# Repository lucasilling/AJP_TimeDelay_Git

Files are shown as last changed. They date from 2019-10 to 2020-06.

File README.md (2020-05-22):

# AJP Time Delay Device Documentation

Supplemental material for article on a programmable electronic delay circuit.

- `assembly-instructions`: A guide to ordering parts and building the device
  yourself.

- `arduino/FIFO_P`: The code uploaded to the Arduino Due.

- `fifo-p3f`: The KiCAD files for the device, as well as a schematic
  PDF and the gerber files that I sent for manufacture.

- `program-rescaling`: The code used to calculate the gain and offset
  resistor values to be optimal, given the constraints of E-series
  values and the overall resistances needed.

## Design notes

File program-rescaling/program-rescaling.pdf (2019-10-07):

# program-rescaling

## August 26, 2019

## 1 Offset and gain calculations for Due DAC to ADC opamps

### 1.1 Voltages that determine required offset and gain

In [1]: V_DL | = 3.3 * 1/6; # V. Due DAC0 minimum voltage
V_DH | = 3.3 * 5/6; # V. Due DAC0 maximum voltage
V_AL | = -2.5; | # V. ADC input minimum voltage
V_AH | = 2.5; | # V. ADC input maximum voltage
offset = ((V_AH + V_AL) - (V_DH + V_DL)) / 2.; # V gain = (V_AH - V_AL) / (V_DH - V_DL); # V/V println("Offset:\t", offset, " V\nGain:\t", gain, " V");
Offset: | -1.65 V
Gain: | 2.2727272727272725 V

### 1.2 Choice of resistor tolerance range (the E-series to use)

In [2]: E3 = [1.0, 2.2, 4.7]; # Very common
E24 = [
| 1.0, 1.1, 1.2, 1.3, 1.5, 1.6, 1.8, 2.0, 2.2, 2.4, 2.7, 3.0, 3.3, 3.6, 3.9, 4.3, 4.7, 5.1, 5.6, 6.2, 6.8, 7.5, 8.2, 9.1

]; # 5% tolerance

In [3]: E_series = E24;

Evaluates f on all possible combinations of resistors in a given E-series.

In [4]: function combinations(E, f)
| span = 1:length(E)
[[f(E[i], E[j]), E[i], E[j]]
| for i in span for j in span] # [[f(x, y), x, y]]
end

Out[4]: combinations (generic function with 1 method)

Finds the nearest E-series value to the value given.

In [5]: function nearest(E, x)
p = floor(log10(x));
y = x / 10^p;
best = first(sort(E, lt = (a, b) -> abs(y - a) < abs(y - b))); best * 10^p;
end

Out[5]: nearest (generic function with 1 method)

### 1.3 Offset component selection calculations

### Improved calculation of the output voltage of the LM4041-ADJ where Vref depends upon VO

(V_Onom here).

In [6]: V_Onom = abs(offset); # V
V_Y = 1.240; # V
∆V_O = V_Onom - V_Y; # V
∆V_ref_∆V_O = -1.55e-3; # V/V. Absolute worst case: -3 mV/V V_ref = V_Y + ∆V_O * ∆V_ref_∆V_O; # V
R2_to_R1 = (V_Onom / V_ref) - 1.; # Ω/Ω

VO(ratio) = V_ref * (ratio + 1.);
println("V_ref = ", V_ref, " V");

V_ref = 1.2393645 V

Selection parameters.

In [7]: ratio_tolerance = 1.; # % RV_off = 1.0e3; # Ω
println("We want a resistor ratio of ", R2_to_R1, " Ω/Ω and ",

ratio_tolerance, "% nominal tolerance.");

We want a resistor ratio of 0.33132746661696366 Ω/Ω and 1.0% nominal tolerance.

Calculate the best resistors to choose to give the best nominal ratio.

In [8]: offset_ratio(x, y, off) = (x + 0.5 * off) / (y + 0.5 * off); # Divide RV_off by 1e3 so that it is at the same scale as the E-series values.
off_ratios | = combinations(E_series,
# [[Ω/Ω, Ω, Ω]]. [[ratio, R2, R1]]

(x, y) -> offset_ratio(x, y, RV_off / 1e3));
off_ratios_tol = filter(x -> ratio_tolerance / 100. > abs(1. - x[1] / R2_to_R1), off_ratios); # [[Ω/Ω, Ω, Ω]]

off_ratios_s = sort(off_ratios_tol, lt = (x, y) -> isless(abs(x[1] - R2_to_R1), abs(y[1] - R2_to_R1))); # [[Ω/Ω, Ω, Ω]]

if (length(off_ratios_s) > 0)
R1 = off_ratios_s[1][3] * 1e3; # Ω
R2 = off_ratios_s[1][2] * 1e3; # Ω

display(off_ratios_s);
println("Best offset resistor values:\n", "R2: ", R2 / 1e3, " kΩ\n",
"R1: ", R1 / 1e3, " kΩ");

else
println("No combinations give a ", ratio_tolerance, "% offset tolerance."); end

3-element Array{Array{Float64,1},1}: [0.333333, 1.1, 4.3]
[0.333333, 2.4, 8.2]
[0.333333, 2.7, 9.1]

Best offset resistor values: R2: 1.1 kΩ
R1: 4.3 kΩ

Calculate the margins of adjustability when a potentiometer is inserted between the two resistors.

In [9]: VO_simple(ratio) = 1.233 * (ratio + 1.);

In [10]: ratio_min = R2 / (R1 + RV_off); ratio_max = (R2 + RV_off) / R1; println("Low:\t", VO(ratio_min), " V"); println("High:\t", VO(ratio_max), " V");
println("S Low:\t", VO_simple(ratio_min), " V");
println("S High:\t", VO_simple(ratio_max), " V");
V_O_low | = VO(ratio_min) - V_Onom; # V. Negative margin away from V_Onom
V_O_high | = VO(ratio_max) - V_Onom; # V. Positive margin away from V_Onom
V_O_total = V_O_high - V_O_low; | # V. Total argin away from V_Onom
println("Offset margins **after amplification** for a ",
RV_off / 1e3, " kΩ potentiometer:\n",
"Low margin:\t", | V_O_low | * 1e3 * gain," mV\t(",
100. * V_O_low | / V_Onom, "%)\n",
"High margin:\t", | V_O_high | * 1e3 * gain, " mV\t(",
100. * V_O_high | / V_Onom, "%)\n",
"Total margin:\t", V_O_total * 1e3 * gain, " mV\t(",
100. * V_O_total / V_Onom, "%)");
Low: | 1.4965910943396226 V
High: | 1.844635534883721 V
S Low: | 1.4889056603773585 V
S High: | 1.8351627906976746 V

Offset margins **after amplification** for a 1.0 kΩ potentiometer:

Low margin: | -348.65660377358483 mV | (-9.297509433962265%)
High margin: | 442.3534883720931 mV | (11.796093023255818%)
Total margin: | 791.010092145678 mV | (21.093602457218083%)

### 1.3.1 LM4041-ADJ resistor selection

In [11]: Vcc_ref = 5.; # V V_R_ref = Vcc_ref - V_Onom; # V R_load = R1 + RV_off + R2; # Ω

I_load = V_Onom / R_load; # A
I_Q = 2.9e-3; # A
I_t = I_Q + I_load;
R_ref = nearest(E_series, V_R_ref / I_t); # Ω

I_ref = V_R_ref / R_ref; # A
println("Best resistor for the LM4041-ADJ (I_load = ", I_load * 1e3, " mA):\n", "R_ref:\t", R_ref / 1e3, " kΩ\n",

"I_ref:\t", I_ref * 1e3, " mA\t(", 100. * (I_ref - I_t) / I_t, "%)\n", "Power:\t", V_R_ref * I_ref * 1e3, " mW");

Best resistor for the LM4041-ADJ (I_load = 0.2578125 mA):
R_ref: | 1.1 kΩ
I_ref: | 3.045454545454546 mA | (-3.558094552651698%)
Power: | 10.202272727272728 mW

### 1.4 Gain component selection calculations

Selection parameters.

In [12]: div_tolerance = 1.; # % RV_gain = 1.0e3 # Ω

#div_nom = 1. / gain;

div_nom = 5.0 / 2.2;
println("We want a resistor divider with a gain of ", div_nom, " V/V and ", div_tolerance, "% nominal tolerance.");

We want a resistor divider with a gain of 2.2727272727272725 V/V and 1.0% nominal tolerance.

Calculate the best resistors to choose to give the best nominal resistor divider.

In [13]: # For noninverting gain configuration
offset_divider(x, y, off) = 1. + (y + 0.5 * off) / (x + 0.5 * off);
# Divide RV_gain by 1e3 so that it is at the same scale as the E-series values. gain_divs = combinations(E_series, # [[Ω/Ω, Ω, Ω]]. [[ratio, Rb, Ra]]

(x, y) -> offset_divider(x, y, RV_gain / 1e3));
gain_divs_tol = filter(x -> div_tolerance / 100. > abs(1. - x[1] / div_nom), gain_divs); # [[Ω/Ω, Ω, Ω]]
gain_divs_s = sort(gain_divs_tol, # [[Ω/Ω, Ω, Ω]]

lt = (x, y) -> isless(abs(x[1] - div_nom), abs(y[1] - div_nom))); if (length(gain_divs_s) > 0)
Ra = gain_divs_s[1][3] * 1e3; # Ω
Rb = gain_divs_s[1][2] * 1e3; # Ω

display(gain_divs_s);
println("Best gain resistor values:\n", "Ra: ", Ra / 1e3, " kΩ\n",
"Rb: ", Rb / 1e3, " kΩ");

else
println("No combinations give a ", div_tolerance, "% gain tolerance."); end

13-element Array{Array{Float64,1},1}: [2.27273, 3.9, 5.1]
[2.27083, 4.3, 5.6]
[2.26829, 3.6, 4.7]
[2.27778, 1.3, 1.8]
[2.28, 2.0, 2.7]
[2.28125, 2.7, 3.6]
[2.26316, 3.3, 4.3]
[2.26087, 1.8, 2.4]
[2.28571, 1.6, 2.2]
[2.25714, 3.0, 3.9]
[2.28846, 4.7, 6.2]
[2.25, 1.1, 1.5]
[2.25, 1.5, 2.0]

Best gain resistor values: Ra: 5.1 kΩ
Rb: 3.9 kΩ

Calculate the margins of adjustability when a potentiometer is inserted between the two resistors.

In [14]: div_min | = Rb / (Ra + Rb + RV_gain);
div_max | = (Rb + RV_gain) / (Ra + Rb + RV_gain);
div_low | = div_min | - div_nom; # V. Negative margin away from V_Onom
div_high | = div_max | - div_nom; # V. Positive margin away from V_Onom
div_total = div_high - div_low; # V. Total margin away from V_Onom println("Gain margins for a ", RV_gain / 1e3, " kΩ potentiometer:\n",
"Low margin:\t", | div_low | * 1e3, " mV\t(",
100. * div_low | / div_nom, "%)\n",
"High margin:\t", | div_high | * 1e3, " mV\t(",
100. * div_high | / div_nom, "%)\n",

"Total margin:\t", div_total * 1e3, " mV\t(",
100. * div_total / div_nom, "%)");

Gain margins for a 1.0 kΩ potentiometer:

Low margin: | -1882.7272727272723 mV | (-82.83999999999999%)
High margin: | -1782.7272727272725 mV | (-78.44%)
Total margin: | 99.99999999999987 mV | (4.399999999999994%)

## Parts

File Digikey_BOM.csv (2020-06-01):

Manufacturer Part Number | Manufacturer | Digi-Key Part Number | Customer Reference | Reference Designator | Packaging | Part Status | Quantity | Unit Price | Extended Price | Quantity Available | Mfg Std Lead Time | Description | RoHS Status | Lead Free Status | REACH Status
LM2940CT-5.0/NOPB | Texas Instruments | LM2940CT-5.0/NOPB-ND |  | U6 | Tube | Active | 1 | 1.53 | $1.53 | 7476 | 6 Weeks | IC REG LINEAR 5V 1A TO220-3 | ROHS3 Compliant | Lead free | REACH Unaffected
LM2776DBVR | Texas Instruments | 296-43957-1-ND |  | U15 | Cut Tape (CT) | Active | 1 | 1.02 | $1.02 | 12481 | 6 Weeks | IC REG CHARGE PUMP INV SOT23 | ROHS3 Compliant | Lead free | REACH Unaffected
AD7840ARSZ | Analog Devices Inc. | AD7840ARSZ-ND |  | U13 | Tube | Active | 1 | 33.39 | $33.39 | 643 | 8 Weeks | IC DAC 14BIT V-OUT 24SSOP | ROHS3 Compliant | Lead free | REACH Unaffected
72V2105L10PFG | Renesas Electronics America Inc. | 800-1511-ND |  | U10 | Tray | Active | 1 | 131.65 | $131.65 | 45 | 13 Weeks | IC FIFO SUPERSYNC 10NS 64-TQFP | ROHS3 Compliant | Lead free | REACH Unaffected
LTC1740CG#PBF | Linear Technology/Analog Devices | LTC1740CG#PBF-ND |  | U5 | Tube | Active | 1 | 41.67 | $41.67 | 53 | 8 Weeks | IC ADC 14BIT PIPELINED 36SSOP | ROHS3 Compliant | Lead free | REACH Unaffected
SN74LVC2G157DCTR | Texas Instruments | 296-13266-1-ND |  | U2 | Cut Tape (CT) | Active | 3 | 0.48 | $1.44 | 3725 | 6 Weeks | IC 2-1LINE DATA SELECT/MUX SM8 | ROHS3 Compliant | Lead free | REACH Unaffected
61C11-01-08-02 | Grayhill Inc. | GH6102-ND |  | SW1 | Bulk | Active | 1 | 25.77 | $25.77 | 559 | 16 Weeks | ROTARY ENCODER OPTICAL 32PPR | RoHS non-compliant | Contains lead | REACH Unaffected
PRPC002SAAN-RC | Sullins Connector Solutions | S1011EC-02-ND | Board to board | U9 | Bag | Active | 2 | 0.08 | $0.16 | 34630 | Not Available | CONN HEADER VERT 2POS 2.54MM | ROHS3 Compliant | Lead free | REACH Unaffected
PJ-002A | CUI Devices | CP-002A-ND |  | J2 | Bag | Active | 1 | 0.6 | $0.60 | 35575 | 11 Weeks | CONN PWR JACK 2X5.5MM SOLDER | RoHS Compliant | Lead free | Not Available
151033RS03000 | Würth Elektronik | 732-5013-ND |  | D1 | Bulk | Active | 1 | 0.17 | $0.17 | 13557 | 14 Weeks | LED RED CLEAR 3MM ROUND T/H | ROHS3 Compliant | Lead free | REACH Unaffected
4440 | Adafruit Industries LLC | 1528-4440-ND | 128x32 OLED | U11 | Bulk | Active | 1 | 12.5 | $12.50 | 1010 | Not Available | I2C OLED DISPLAY STEMMA QWIIC | ROHS3 Compliant | Not Available | Not Available
A000062 | Arduino | 1050-1049-ND |  | U9 | Box | Active | 1 | 37.4 | $37.40 | 653 | Not Available | ARDUINO DUE ATSAM3X8E EVAL BRD | RoHS Compliant | Lead free | Not Available
5-1634503-1 | TE Connectivity AMP Connectors | A97581-ND |  | J1, J4, J5, J7, J8 | Box | Active | 5 | 2.25 | $11.25 | 11968 | Not Available | CONN BNC JACK STR 50 OHM PCB | RoHS Compliant | Lead free | Not Available
TS12A12511DCNR | Texas Instruments | 296-27523-1-ND |  | U1 | Cut Tape (CT) | Active | 1 | 1.45 | $1.45 | 11236 | 6 Weeks | IC SWITCH SGL SPDT ANLG SOT23-8 | ROHS3 Compliant | Lead free | REACH Unaffected
LM4041DYM3-ADJ-TR | Microchip Technology | 576-2573-1-ND |  | U14 | Cut Tape (CT) | Active | 1 | 0.29 | $0.29 | 2170 | 4 Weeks | IC VREF SHUNT 10V 1% SOT23-3 | ROHS3 Compliant | Lead free | REACH Unaffected
TS53YL102MR10 | Vishay Sfernice | TS53YL-1.0KCT-ND |  | RV1, RV3 | Cut Tape (CT) | Active | 2 | 1.87 | $3.74 | 5901 | 17 Weeks | TRIMMER 1K OHM 0.25W GW TOP ADJ | ROHS3 Compliant | Lead free | Not Available
DMP3099L-7 | Diodes Incorporated | DMP3099L-7DICT-ND |  | Q1 | Cut Tape (CT) | Active | 1 | 0.33 | $0.33 | 183767 | 23 Weeks | MOSFET P-CH 30V SOT23 | ROHS3 Compliant | Lead free | REACH Unaffected
SN74LVC1G04DBVR | Texas Instruments | 296-11599-1-ND |  | U7 | Cut Tape (CT) | Active | 1 | 0.32 | $0.32 | 85313 | 6 Weeks | IC INVERTER 1CH 1-INP SOT23-5 | ROHS3 Compliant | Lead free | REACH Unaffected
SN74LVC1G08DBVR | Texas Instruments | 296-11601-1-ND |  | U12 | Cut Tape (CT) | Active | 1 | 0.26 | $0.26 | 97419 | 6 Weeks | IC GATE AND 1CH 2-INP SOT23-5 | ROHS3 Compliant | Lead free | REACH Unaffected
08055C104KAT2A | AVX Corporation | 478-1395-1-ND | 0u1 | C8, C9, C10, C15, C16, C22, C46,C23, C28, C30, C32, C37, C38 | Cut Tape (CT) | Active | 20 | 0.083 | $1.66 | 36630219 | 12 Weeks | CAP CER 0.1UF 50V X7R 0805 | ROHS3 Compliant | Lead free | REACH Unaffected
08053C105KAT2A | AVX Corporation | 478-5030-1-ND | 1u | C1, C3, C4, C6, C19, C20, C40, C41,C11, C12, C13, C14, C21, C25, C35, C39 | Cut Tape (CT) | Active | 20 | 0.176 | $3.52 | 559518 | 16 Weeks | CAP CER 1UF 25V X7R 0805 | ROHS3 Compliant | Lead free | REACH Unaffected
CL21A106KAYNNNE | Samsung Electro-Mechanics | 1276-2891-1-ND | 10u | C5, C7, C17, C18, C26, C27, C42, C43, C44, C45,C24, C29, C31, C33 | Cut Tape (CT) | Active | 20 | 0.19 | $3.80 | 2116302 | 22 Weeks | CAP CER 10UF 25V X5R 0805 | ROHS3 Compliant | Lead free | REACH Unaffected
08055A102JAT2A | AVX Corporation | 478-1328-1-ND | 1n | C2,C34, C47 | Cut Tape (CT) | Active | 10 | 0.126 | $1.26 | 303649 | 12 Weeks | CAP CER 1000PF 50V C0G/NP0 0805 | ROHS3 Compliant | Lead free | REACH Unaffected
RC0805FR-0749R9L | Yageo | 311-49.9CRCT-ND |  | R1, R3, R4, R19 | Cut Tape (CT) | Active | 4 | 0.1 | $0.40 | 1707550 | 33 Weeks | RES SMD 49.9 OHM 1% 1/8W 0805 | ROHS3 Compliant | Lead free | REACH Unaffected
RC0805FR-0722RL | Yageo | 311-22.0CRCT-ND |  | R2, R6, R20 | Cut Tape (CT) | Active | 3 | 0.1 | $0.30 | 235480 | 33 Weeks | RES SMD 22 OHM 1% 1/8W 0805 | ROHS3 Compliant | Lead free | REACH Unaffected
RC0805FR-07220RL | Yageo | 311-220CRCT-ND |  | R5 | Cut Tape (CT) | Active | 1 | 0.1 | $0.10 | 1267440 | 33 Weeks | RES SMD 220 OHM 1% 1/8W 0805 | ROHS3 Compliant | Lead free | REACH Unaffected
RC0805FR-075K1L | Yageo | 311-5.10KCRCT-ND |  | R7, R9, R10, R11, R13, R16, R17, R18 | Cut Tape (CT) | Active | 10 | 0.04 | $0.40 | 2672 | 33 Weeks | RES SMD 5.1K OHM 1% 1/8W 0805 | ROHS3 Compliant | Lead free | REACH Unaffected
RC0805FR-071K1L | Yageo | 311-1.10KCRCT-ND |  | R8, R14 | Cut Tape (CT) | Active | 2 | 0.1 | $0.20 | 745483 | 33 Weeks | RES SMD 1.1K OHM 1% 1/8W 0805 | ROHS3 Compliant | Lead free | REACH Unaffected
RC0805FR-073K9L | Yageo | 311-3.90KCRCT-ND |  | R15 | Cut Tape (CT) | Active | 1 | 0.1 | $0.10 | 643670 | 33 Weeks | RES SMD 3.9K OHM 1% 1/8W 0805 | ROHS3 Compliant | Lead free | REACH Unaffected
RC0805FR-074K3L | Yageo | 311-4.30KCRCT-ND |  | R12 | Cut Tape (CT) | Active | 1 | 0.1 | $0.10 | 238177 | 33 Weeks | RES SMD 4.3K OHM 1% 1/8W 0805 | ROHS3 Compliant | Lead free | REACH Unaffected
LM1117IDTX-3.3/NOPB | Texas Instruments | LM1117IDTX-3.3/NOPBCT-ND |  | U8 | Cut Tape (CT) | Active | 1 | 1.44 | $1.44 | 21823 | 6 Weeks | IC REG LINEAR 3.3V 800MA TO252-3 | ROHS3 Compliant | Lead free | REACH Unaffected
TL082CDR | Texas Instruments | 296-1284-1-ND |  | U16 | Cut Tape (CT) | Active | 1 | 0.41 | $0.41 | 12716 | 6 Weeks | IC OPAMP JFET 2 CIRCUIT 8SOIC | ROHS3 Compliant | Lead free | REACH Unaffected
OSTTC082162 | On Shore Technology Inc. | ED2615-ND |  | J3 | Bulk | Active | 1 | 1.72 | $1.72 | 1723 | 8 Weeks | TERM BLK 8P SIDE ENT 5.08MM PCB | ROHS3 Compliant | Lead free | REACH Unaffected
54102-S08-18 | Amphenol ICC (FCI) | 609-5600-ND | Board to board | U9 | Bulk | Active | 1 | 1.45 | $1.45 | 197 | 9 Weeks | CONN HEADER VERT 36POS 2.54MM | RoHS non-compliant | Contains lead | Not Available
PRPC003SAAN-RC | Sullins Connector Solutions | S1011EC-03-ND | Board to board | U9 | Bag | Active | 1 | 0.12 | $0.12 | 11543 | Not Available | CONN HEADER VERT 3POS 2.54MM | ROHS3 Compliant | Lead free | REACH Unaffected
PRPC006SAAN-RC | Sullins Connector Solutions | S1011EC-06-ND | Board to board | U9 | Bag | Active | 1 | 0.19 | $0.19 | 2550 | Not Available | CONN HEADER VERT 6POS 2.54MM | ROHS3 Compliant | Lead free | REACH Unaffected
LPPB042CFFN-RC | Sullins Connector Solutions | S9009E-04-ND | Board to board | U9 | Tube | Active | 1 | 1.05 | $1.05 | 2828 | 5 Weeks | CONN HDR 8POS 0.05 GOLD PCB | ROHS3 Compliant | Lead free | REACH Unaffected
RC0805JR-070RL | Yageo | 311-0.0ARCT-ND | Jumpers |  | Cut Tape (CT) | Active | 10 | 0.035 | $0.35 | 11238049 | 24 Weeks | RES SMD 0 OHM JUMPER 1/8W 0805 | ROHS3 Compliant | Lead free | REACH Unaffected
3296W-1-103LF | Bourns Inc. | 3296W-103LF-ND |  | RV2 | Tube | Active | 1 | 2.41 | $2.41 | 4469 | 6 Weeks | TRIMMER 10K OHM 0.5W PC PIN TOP | ROHS3 Compliant | Lead free | REACH Unaffected

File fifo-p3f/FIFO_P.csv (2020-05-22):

Source: | /home/jfjhh/Documents/AJP_TimeDelay_Git/fifo-p3f/FIFO_P.sch
Date: | Thu 21 May 2020 10:44:45 PM EDT
Tool: | Eeschema 5.1.6
Generator: | /usr/share/kicad/plugins/bom_csv_grouped_by_value.py
Component Count: | 96
Individual Components:
Item | Qty | Reference(s) | Value | LibPart | Footprint | Datasheet
 |  | C1 | 1u | Device:C_Small | Capacitor_SMD:C_0805_2012Metric_Pad1.15x1.40mm_HandSolder
 |  | C2 | 1n | Device:C_Small | Capacitor_SMD:C_0805_2012Metric_Pad1.15x1.40mm_HandSolder
 |  | C3 | 1u | Device:C_Small | Capacitor_SMD:C_0805_2012Metric_Pad1.15x1.40mm_HandSolder
 |  | C4 | 1u | Device:C_Small | Capacitor_SMD:C_0805_2012Metric_Pad1.15x1.40mm_HandSolder
 |  | C5 | 10u | Device:C | Capacitor_SMD:C_0805_2012Metric_Pad1.15x1.40mm_HandSolder
 |  | C6 | 1u | Device:C_Small | Capacitor_SMD:C_0805_2012Metric_Pad1.15x1.40mm_HandSolder
 |  | C7 | 10u | Device:C | Capacitor_SMD:C_0805_2012Metric_Pad1.15x1.40mm_HandSolder
 |  | C8 | 0u1 | Device:C | Capacitor_SMD:C_0805_2012Metric_Pad1.15x1.40mm_HandSolder
 |  | C9 | 0u1 | Device:C | Capacitor_SMD:C_0805_2012Metric_Pad1.15x1.40mm_HandSolder
 |  | C10 | 0u1 | Device:C | Capacitor_SMD:C_0805_2012Metric_Pad1.15x1.40mm_HandSolder
 |  | C11 | 1u | Device:C | Capacitor_SMD:C_0805_2012Metric_Pad1.15x1.40mm_HandSolder
 |  | C12 | 1u | Device:C | Capacitor_SMD:C_0805_2012Metric_Pad1.15x1.40mm_HandSolder
 |  | C13 | 1u | Device:C | Capacitor_SMD:C_0805_2012Metric_Pad1.15x1.40mm_HandSolder
 |  | C14 | 1u | Device:C | Capacitor_SMD:C_0805_2012Metric_Pad1.15x1.40mm_HandSolder
 |  | C15 | 0u1 | Device:C | Capacitor_SMD:C_0805_2012Metric_Pad1.15x1.40mm_HandSolder | ~
 |  | C16 | 0u1 | Device:C | Capacitor_SMD:C_0805_2012Metric_Pad1.15x1.40mm_HandSolder | ~
 |  | C17 | 10u | Device:C | Capacitor_SMD:C_0805_2012Metric_Pad1.15x1.40mm_HandSolder
 |  | C18 | 10u | Device:C | Capacitor_SMD:C_0805_2012Metric_Pad1.15x1.40mm_HandSolder
 |  | C19 | 1u | Device:C_Small | Capacitor_SMD:C_0805_2012Metric_Pad1.15x1.40mm_HandSolder
 |  | C20 | 1u | Device:C_Small | Capacitor_SMD:C_0805_2012Metric_Pad1.15x1.40mm_HandSolder
 |  | C21 | 1u | Device:C | Capacitor_SMD:C_0805_2012Metric_Pad1.15x1.40mm_HandSolder
 |  | C22 | 0u1 | Device:C | Capacitor_SMD:C_0805_2012Metric_Pad1.15x1.40mm_HandSolder | ~
 |  | C23 | 0u1 | Device:C_Small | Capacitor_SMD:C_0805_2012Metric_Pad1.15x1.40mm_HandSolder
 |  | C24 | 10u | Device:C_Small | Capacitor_SMD:C_0805_2012Metric_Pad1.15x1.40mm_HandSolder
 |  | C25 | 1u | Device:C | Capacitor_SMD:C_0805_2012Metric_Pad1.15x1.40mm_HandSolder
 |  | C26 | 10u | Device:C | Capacitor_SMD:C_0805_2012Metric_Pad1.15x1.40mm_HandSolder
 |  | C27 | 10u | Device:C | Capacitor_SMD:C_0805_2012Metric_Pad1.15x1.40mm_HandSolder
 |  | C28 | 0u1 | Device:C_Small | Capacitor_SMD:C_0805_2012Metric_Pad1.15x1.40mm_HandSolder
 |  | C29 | 10u | Device:C_Small | Capacitor_SMD:C_0805_2012Metric_Pad1.15x1.40mm_HandSolder
 |  | C30 | 0u1 | Device:C_Small | Capacitor_SMD:C_0805_2012Metric_Pad1.15x1.40mm_HandSolder
 |  | C31 | 10u | Device:C_Small | Capacitor_SMD:C_0805_2012Metric_Pad1.15x1.40mm_HandSolder
 |  | C32 | 0u1 | Device:C_Small | Capacitor_SMD:C_0805_2012Metric_Pad1.15x1.40mm_HandSolder
 |  | C33 | 10u | Device:C_Small | Capacitor_SMD:C_0805_2012Metric_Pad1.15x1.40mm_HandSolder
 |  | C34 | 1n | Device:C | Capacitor_SMD:C_0805_2012Metric_Pad1.15x1.40mm_HandSolder | ~
 |  | C35 | 1u | Device:C | Capacitor_SMD:C_0805_2012Metric_Pad1.15x1.40mm_HandSolder | ~
 |  | C37 | 0u1 | Device:C_Small | Capacitor_SMD:C_0805_2012Metric_Pad1.15x1.40mm_HandSolder | ~
 |  | C38 | 0u1 | Device:C_Small | Capacitor_SMD:C_0805_2012Metric_Pad1.15x1.40mm_HandSolder | ~
 |  | C39 | 1u | Device:C | Capacitor_SMD:C_0805_2012Metric_Pad1.15x1.40mm_HandSolder | ~
 |  | C40 | 1u | Device:C_Small | Capacitor_SMD:C_0805_2012Metric_Pad1.15x1.40mm_HandSolder | ~
 |  | C41 | 1u | Device:C_Small | Capacitor_SMD:C_0805_2012Metric_Pad1.15x1.40mm_HandSolder | ~
 |  | C42 | 10u | Device:C | Capacitor_SMD:C_0805_2012Metric_Pad1.15x1.40mm_HandSolder | ~
 |  | C43 | 10u | Device:C | Capacitor_SMD:C_0805_2012Metric_Pad1.15x1.40mm_HandSolder | ~
 |  | C44 | 10u | Device:C | Capacitor_SMD:C_0805_2012Metric_Pad1.15x1.40mm_HandSolder | ~
 |  | C45 | 10u | Device:C | Capacitor_SMD:C_0805_2012Metric_Pad1.15x1.40mm_HandSolder | ~
 |  | C46 | 0u1 | Device:C | Capacitor_SMD:C_0805_2012Metric_Pad1.15x1.40mm_HandSolder | ~
 |  | C47 | 1n | Device:C | Capacitor_SMD:C_0805_2012Metric_Pad1.15x1.40mm_HandSolder | ~
 |  | D1 | LED_RED | Device:LED | LED_THT:LED_D3.0mm
 |  | J1 | Vin | Connector:Conn_Coaxial | Connector_Coaxial:BNC_TEConnectivity_1478204_Vertical | ~
 |  | J2 | Jack-DC | Connector:Jack-DC | Connector_BarrelJack:BarrelJack_Horizontal | ~
 |  | J3 | Screw_Terminal_01x08 | Connector:Screw_Terminal_01x08 | TerminalBlock_Phoenix:TerminalBlock_Phoenix_MKDS-3-8-5.08_1x08_P5.08mm_Horizontal | ~
 |  | J4 | XWCLK | Connector:Conn_Coaxial | Connector_Coaxial:BNC_TEConnectivity_1478204_Vertical | ~
 |  | J5 | XRCLK | Connector:Conn_Coaxial | Connector_Coaxial:BNC_TEConnectivity_1478204_Vertical | ~
 |  | J6 | Conn_02x04_Odd_Even | Connector_Generic:Conn_02x04_Odd_Even | Connector_PinSocket_1.27mm:PinSocket_2x04_P1.27mm_Vertical | ~
 |  | J7 | Start Trigger | Connector:Conn_Coaxial | Connector_Coaxial:BNC_TEConnectivity_1478204_Vertical | ~
 |  | J8 | Vout | Connector:Conn_Coaxial | Connector_Coaxial:BNC_TEConnectivity_1478204_Vertical | ~
 |  | Q1 | DMP3099L | FIFO_P:DMP3099L | Package_TO_SOT_SMD:SOT-23 | https://www.diodes.com/assets/Datasheets/DMP3013SFV.pdf
 |  | R1 | 49R9 | Device:R | Resistor_SMD:R_0805_2012Metric_Pad1.15x1.40mm_HandSolder
 |  | R2 | 22R | Device:R | Resistor_SMD:R_0805_2012Metric_Pad1.15x1.40mm_HandSolder | ~
 |  | R3 | 49R9 | Device:R | Resistor_SMD:R_0805_2012Metric_Pad1.15x1.40mm_HandSolder
 |  | R4 | 49R9 | Device:R | Resistor_SMD:R_0805_2012Metric_Pad1.15x1.40mm_HandSolder
 |  | R5 | 220R | Device:R | Resistor_SMD:R_0805_2012Metric_Pad1.15x1.40mm_HandSolder
 |  | R6 | 22R | Device:R | Resistor_SMD:R_0805_2012Metric_Pad1.15x1.40mm_HandSolder | ~
 |  | R7 | 5k1 | Device:R | Resistor_SMD:R_0805_2012Metric_Pad1.15x1.40mm_HandSolder
 |  | R8 | 1k1 | Device:R | Resistor_SMD:R_0805_2012Metric_Pad1.15x1.40mm_HandSolder | ~
 |  | R9 | 5k1 | Device:R | Resistor_SMD:R_0805_2012Metric_Pad1.15x1.40mm_HandSolder
 |  | R10 | 5k1 | Device:R | Resistor_SMD:R_0805_2012Metric_Pad1.15x1.40mm_HandSolder
 |  | R11 | 5k1 | Device:R | Resistor_SMD:R_0805_2012Metric_Pad1.15x1.40mm_HandSolder | ~
 |  | R12 | 4k3 | Device:R | Resistor_SMD:R_0805_2012Metric_Pad1.15x1.40mm_HandSolder | ~
 |  | R13 | 5k1 | Device:R | Resistor_SMD:R_0805_2012Metric_Pad1.15x1.40mm_HandSolder | ~
 |  | R14 | 1k1 | Device:R | Resistor_SMD:R_0805_2012Metric_Pad1.15x1.40mm_HandSolder | ~
 |  | R15 | 3k9 | Device:R | Resistor_SMD:R_0805_2012Metric_Pad1.15x1.40mm_HandSolder | ~
 |  | R16 | 5k1 | Device:R | Resistor_SMD:R_0805_2012Metric_Pad1.15x1.40mm_HandSolder | ~
 |  | R17 | 5k1 | Device:R | Resistor_SMD:R_0805_2012Metric_Pad1.15x1.40mm_HandSolder | ~
 |  | R18 | 5k1 | Device:R | Resistor_SMD:R_0805_2012Metric_Pad1.15x1.40mm_HandSolder | ~
 |  | R19 | 49R9 | Device:R | Resistor_SMD:R_0805_2012Metric_Pad1.15x1.40mm_HandSolder | ~
 |  | R20 | 22R | Device:R | Resistor_SMD:R_0805_2012Metric_Pad1.15x1.40mm_HandSolder | ~
 |  | RV1 | 1k | Device:R_POT | Potentiometer_SMD:Potentiometer_Vishay_TS53YL_Vertical | ~
 |  | RV2 | 10k | Device:R_POT | Potentiometer_THT:Potentiometer_Bourns_3296W_Vertical | ~
 |  | RV3 | 1k | Device:R_POT | Potentiometer_SMD:Potentiometer_Vishay_TS53YL_Vertical | ~
 |  | SW1 | Rotary_Encoder_61C | FIFO_P:Rotary_Encoder_61C | FIFO_P:Rotary_Encoder_61C
 |  | U1 | TS12A12511 | FIFO_P:TS12A12511 | Package_TO_SOT_SMD:SOT-23-8_Handsoldering
 |  | U2 | SN74LVC2G157_MUX_TI | FIFO_P:SN74LVC2G157_MUX_TI | Package_SO:SSOP-8_2.95x2.8mm_P0.65mm
 |  | U3 | SN74LVC2G157_MUX_TI | FIFO_P:SN74LVC2G157_MUX_TI | Package_SO:SSOP-8_2.95x2.8mm_P0.65mm
 |  | U4 | SN74LVC2G157_MUX_TI | FIFO_P:SN74LVC2G157_MUX_TI | Package_SO:SSOP-8_2.95x2.8mm_P0.65mm
 |  | U5 | LTC1740 | FIFO_P:LTC1740 | FIFO_P:SSOP-36_5.3mm_Pitch0.65mm
 |  | U6 | LM2940CT-5.0 | FIFO_P:LM2940CT-5.0 | Package_TO_SOT_THT:TO-220-3_Horizontal_TabDown
 |  | U7 | 74LVC1G04 | 74xGxx:74LVC1G04 | Package_TO_SOT_SMD:SOT-23-5_HandSoldering | http://www.ti.com/lit/sg/scyt129e/scyt129e.pdf
 |  | U8 | LM1117-3.3 | Regulator_Linear:LM1117-3.3 | Package_TO_SOT_SMD:TO-252-3_TabPin2 | http://www.ti.com/lit/ds/symlink/lm1117.pdf
 |  | U9 | ARDUINO_DUE_FIFO_P_COMMANDS | FIFO_P:ARDUINO_DUE_FIFO_P_COMMANDS | FIFO_P:Arduino_Due_Selected_Pins
 |  | U10 | IDT_72V2105 | FIFO_P:IDT_72V2105 | FIFO_P:LQFP-64_14x14mm_P0.8mm_HandSolder
 |  | U11 | Adafruit_128x32_OLED_I2C_1306 | FIFO_P:Adafruit_128x32_OLED_I2C_1306 | FIFO_P:Adafruit_128x32_OLED_I2C_1306
 |  | U12 | 74LVC1G08 | 74xGxx:74LVC1G08 | Package_TO_SOT_SMD:SOT-23-5_HandSoldering | http://www.ti.com/lit/sg/scyt129e/scyt129e.pdf
 |  | U13 | AD7840 | FIFO_P:AD7840 | Package_SO:SSOP-24_5.3x8.2mm_P0.65mm
 |  | U14 | LM4041LP-ADJ | Reference_Voltage:LM4041LP-ADJ | Package_TO_SOT_SMD:SOT-23_Handsoldering | http://www.ti.com/lit/ds/symlink/lm4041-n.pdf
 |  | U15 | LM2776 | Regulator_SwitchedCapacitor:LM2776 | Package_TO_SOT_SMD:SOT-23-6 | http://www.ti.com/lit/ds/symlink/lm2776.pdf
 |  | U16 | TL082 | Amplifier_Operational:TL082 | Package_SO:SOIC-8_3.9x4.9mm_P1.27mm | http://www.ti.com/lit/ds/symlink/tl081.pdf
Collated Components:
Item | Qty | Reference(s) | Value | LibPart | Footprint | Datasheet
1 | 8 | C1, C3, C4, C6, C19, C20, C40, C41 | 1u | Device:C_Small | Capacitor_SMD:C_0805_2012Metric_Pad1.15x1.40mm_HandSolder | ~
2 | 1 | C2 | 1n | Device:C_Small | Capacitor_SMD:C_0805_2012Metric_Pad1.15x1.40mm_HandSolder
3 | 10 | C5, C7, C17, C18, C26, C27, C42, C43, C44, C45 | 10u | Device:C | Capacitor_SMD:C_0805_2012Metric_Pad1.15x1.40mm_HandSolder | ~
4 | 7 | C8, C9, C10, C15, C16, C22, C46 | 0u1 | Device:C | Capacitor_SMD:C_0805_2012Metric_Pad1.15x1.40mm_HandSolder | ~
5 | 8 | C11, C12, C13, C14, C21, C25, C35, C39 | 1u | Device:C | Capacitor_SMD:C_0805_2012Metric_Pad1.15x1.40mm_HandSolder | ~
6 | 6 | C23, C28, C30, C32, C37, C38 | 0u1 | Device:C_Small | Capacitor_SMD:C_0805_2012Metric_Pad1.15x1.40mm_HandSolder | ~
7 | 4 | C24, C29, C31, C33 | 10u | Device:C_Small | Capacitor_SMD:C_0805_2012Metric_Pad1.15x1.40mm_HandSolder
8 | 2 | C34, C47 | 1n | Device:C | Capacitor_SMD:C_0805_2012Metric_Pad1.15x1.40mm_HandSolder | ~
9 | 1 | D1 | LED_RED | Device:LED | LED_THT:LED_D3.0mm
10 | 1 | J1 | Vin | Connector:Conn_Coaxial | Connector_Coaxial:BNC_TEConnectivity_1478204_Vertical | ~
11 | 1 | J2 | Jack-DC | Connector:Jack-DC | Connector_BarrelJack:BarrelJack_Horizontal | ~
12 | 1 | J3 | Screw_Terminal_01x08 | Connector:Screw_Terminal_01x08 | TerminalBlock_Phoenix:TerminalBlock_Phoenix_MKDS-3-8-5.08_1x08_P5.08mm_Horizontal | ~
13 | 1 | J4 | XWCLK | Connector:Conn_Coaxial | Connector_Coaxial:BNC_TEConnectivity_1478204_Vertical | ~
14 | 1 | J5 | XRCLK | Connector:Conn_Coaxial | Connector_Coaxial:BNC_TEConnectivity_1478204_Vertical | ~
15 | 1 | J6 | Conn_02x04_Odd_Even | Connector_Generic:Conn_02x04_Odd_Even | Connector_PinSocket_1.27mm:PinSocket_2x04_P1.27mm_Vertical | ~
16 | 1 | J7 | Start Trigger | Connector:Conn_Coaxial | Connector_Coaxial:BNC_TEConnectivity_1478204_Vertical | ~
17 | 1 | J8 | Vout | Connector:Conn_Coaxial | Connector_Coaxial:BNC_TEConnectivity_1478204_Vertical | ~
18 | 1 | Q1 | DMP3099L | FIFO_P:DMP3099L | Package_TO_SOT_SMD:SOT-23 | https://www.diodes.com/assets/Datasheets/DMP3013SFV.pdf
19 | 4 | R1, R3, R4, R19 | 49R9 | Device:R | Resistor_SMD:R_0805_2012Metric_Pad1.15x1.40mm_HandSolder | ~
20 | 3 | R2, R6, R20 | 22R | Device:R | Resistor_SMD:R_0805_2012Metric_Pad1.15x1.40mm_HandSolder | ~
21 | 1 | R5 | 220R | Device:R | Resistor_SMD:R_0805_2012Metric_Pad1.15x1.40mm_HandSolder
22 | 8 | R7, R9, R10, R11, R13, R16, R17, R18 | 5k1 | Device:R | Resistor_SMD:R_0805_2012Metric_Pad1.15x1.40mm_HandSolder | ~
23 | 2 | R8, R14 | 1k1 | Device:R | Resistor_SMD:R_0805_2012Metric_Pad1.15x1.40mm_HandSolder | ~
24 | 1 | R12 | 4k3 | Device:R | Resistor_SMD:R_0805_2012Metric_Pad1.15x1.40mm_HandSolder | ~
25 | 1 | R15 | 3k9 | Device:R | Resistor_SMD:R_0805_2012Metric_Pad1.15x1.40mm_HandSolder | ~
26 | 2 | RV1, RV3 | 1k | Device:R_POT | Potentiometer_SMD:Potentiometer_Vishay_TS53YL_Vertical | ~
27 | 1 | RV2 | 10k | Device:R_POT | Potentiometer_THT:Potentiometer_Bourns_3296W_Vertical | ~
28 | 1 | SW1 | Rotary_Encoder_61C | FIFO_P:Rotary_Encoder_61C | FIFO_P:Rotary_Encoder_61C
29 | 1 | U1 | TS12A12511 | FIFO_P:TS12A12511 | Package_TO_SOT_SMD:SOT-23-8_Handsoldering
30 | 3 | U2, U3, U4 | SN74LVC2G157_MUX_TI | FIFO_P:SN74LVC2G157_MUX_TI | Package_SO:SSOP-8_2.95x2.8mm_P0.65mm
31 | 1 | U5 | LTC1740 | FIFO_P:LTC1740 | FIFO_P:SSOP-36_5.3mm_Pitch0.65mm
32 | 1 | U6 | LM2940CT-5.0 | FIFO_P:LM2940CT-5.0 | Package_TO_SOT_THT:TO-220-3_Horizontal_TabDown
33 | 1 | U7 | 74LVC1G04 | 74xGxx:74LVC1G04 | Package_TO_SOT_SMD:SOT-23-5_HandSoldering | http://www.ti.com/lit/sg/scyt129e/scyt129e.pdf
34 | 1 | U8 | LM1117-3.3 | Regulator_Linear:LM1117-3.3 | Package_TO_SOT_SMD:TO-252-3_TabPin2 | http://www.ti.com/lit/ds/symlink/lm1117.pdf
35 | 1 | U9 | ARDUINO_DUE_FIFO_P_COMMANDS | FIFO_P:ARDUINO_DUE_FIFO_P_COMMANDS | FIFO_P:Arduino_Due_Selected_Pins
36 | 1 | U10 | IDT_72V2105 | FIFO_P:IDT_72V2105 | FIFO_P:LQFP-64_14x14mm_P0.8mm_HandSolder
37 | 1 | U11 | Adafruit_128x32_OLED_I2C_1306 | FIFO_P:Adafruit_128x32_OLED_I2C_1306 | FIFO_P:Adafruit_128x32_OLED_I2C_1306
38 | 1 | U12 | 74LVC1G08 | 74xGxx:74LVC1G08 | Package_TO_SOT_SMD:SOT-23-5_HandSoldering | http://www.ti.com/lit/sg/scyt129e/scyt129e.pdf
39 | 1 | U13 | AD7840 | FIFO_P:AD7840 | Package_SO:SSOP-24_5.3x8.2mm_P0.65mm
40 | 1 | U14 | LM4041LP-ADJ | Reference_Voltage:LM4041LP-ADJ | Package_TO_SOT_SMD:SOT-23_Handsoldering | http://www.ti.com/lit/ds/symlink/lm4041-n.pdf
41 | 1 | U15 | LM2776 | Regulator_SwitchedCapacitor:LM2776 | Package_TO_SOT_SMD:SOT-23-6 | http://www.ti.com/lit/ds/symlink/lm2776.pdf
42 | 1 | U16 | TL082 | Amplifier_Operational:TL082 | Package_SO:SOIC-8_3.9x4.9mm_P1.27mm | http://www.ti.com/lit/ds/symlink/tl081.pdf

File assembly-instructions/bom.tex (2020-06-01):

\begin{tabular}{llllll}
\toprule
Manufacturer Part Number & Digi-Key Part Number& Customer Reference & Reference Designator                                                  & Quantity & Extended Price \\
\midrule
LM2940CT-5.0/NOPB   & LM2940CT-5.0/NOPB-ND     &                & U6                                                                        & 1    & 1.53   \\
LM2776DBVR          & 296-43957-1-ND           &                & U15                                                                       & 1    & 1.02   \\
AD7840ARSZ          & AD7840ARSZ-ND            &                & U13                                                                       & 1    & 33.39  \\
72V2105L10PFG       & 800-1511-ND              &                & U10                                                                       & 1    & 131.65 \\
LTC1740CG\#PBF      & LTC1740CG\#PBF-ND        &                & U5                                                                        & 1    & 41.67  \\
SN74LVC2G157DCTR    & 296-13266-1-ND           &                & U2                                                                        & 3    & 1.44   \\
4440                & 1528-4440-ND             & 128x32 OLED    & U11                                                                       & 1    & 12.50  \\
TS12A12511DCNR      & 296-27523-1-ND           &                & U1                                                                        & 1    & 1.45   \\
LM4041DYM3-ADJ-TR   & 576-2573-1-ND            &                & U14                                                                       & 1    & 0.29   \\
SN74LVC1G04DBVR     & 296-11599-1-ND           &                & U7                                                                        & 1    & 0.32   \\
SN74LVC1G08DBVR     & 296-11601-1-ND           &                & U12                                                                       & 1    & 0.26   \\
LM1117IDTX-3.3/NOPB & LM1117IDTX-3.3/NOPBCT-ND &                & U8                                                                        & 1    & 1.44   \\
TL082CDR            & 296-1284-1-ND            &                & U16                                                                       & 1    & 0.41   \\
A000062             & 1050-1049-ND             &                & U9                                                                        & 1    & 37.40  \\
PRPC002SAAN-RC      & S1011EC-02-ND            & Board to board & U9                                                                        & 2    & 0.16   \\
54102-S08-18        & 609-5600-ND              & Board to board & U9                                                                        & 1    & 1.45   \\
PRPC003SAAN-RC      & S1011EC-03-ND            & Board to board & U9                                                                        & 1    & 0.12   \\
PRPC006SAAN-RC      & S1011EC-06-ND            & Board to board & U9                                                                        & 1    & 0.19   \\
LPPB042CFFN-RC      & S9009E-04-ND             & Board to board & U9                                                                        & 1    & 1.05   \\
DMP3099L-7          & DMP3099L-7DICT-ND        &                & Q1                                                                        & 1    & 0.33   \\
151033RS03000       & 732-5013-ND              &                & D1                                                                        & 1    & 0.17   \\
61C11-01-08-02      & GH6102-ND                &                & SW1                                                                       & 1    & 25.77  \\
5-1634503-1         & A97581-ND                &                & J1, J4, J5, J7, J8                                                        & 5    & 11.25  \\
PJ-002A             & CP-002A-ND               &                & J2                                                                        & 1    & 0.60   \\
OSTTC082162         & ED2615-ND                &                & J3                                                                        & 1    & 1.72   \\
TS53YL102MR10       & TS53YL-1.0KCT-ND         &                & RV1, RV3                                                                  & 2    & 3.74   \\
3296W-1-103LF       & 3296W-103LF-ND           &                & RV2                                                                       & 1    & 2.41   \\
RC0805FR-0749R9L    & 311-49.9CRCT-ND          &                & R1, R3, R4, R19                                                           & 4    & 0.40   \\
RC0805FR-0722RL     & 311-22.0CRCT-ND          &                & R2, R6, R20                                                               & 3    & 0.30   \\
RC0805FR-07220RL    & 311-220CRCT-ND           &                & R5                                                                        & 1    & 0.10   \\
RC0805FR-075K1L     & 311-5.10KCRCT-ND         &                & R7, R9, R10, R11, R13, R16, R17, R18                                      & 10   & 0.40   \\
RC0805FR-071K1L     & 311-1.10KCRCT-ND         &                & R8, R14                                                                   & 2    & 0.20   \\
RC0805FR-073K9L     & 311-3.90KCRCT-ND         &                & R15                                                                       & 1    & 0.10   \\
RC0805FR-074K3L     & 311-4.30KCRCT-ND         &                & R12                                                                       & 1    & 0.10   \\
RC0805JR-070RL      & 311-0.0ARCT-ND           & Jumpers        &                                                                           & 10   & 0.35   \\
08055C104KAT2A      & 478-1395-1-ND            & 0u1            & C8, C9, C10, C15, C16, C22, C46,C23, C28, C30, C32, C37, C38              & 20   & 1.66   \\
08053C105KAT2A      & 478-5030-1-ND            & 1u             & C1, C3, C4, C6, C19, C20, C40, C41,C11, C12, C13, C14, C21, C25, C35, C39 & 20   & 3.52   \\
CL21A106KAYNNNE     & 1276-2891-1-ND           & 10u            & C5, C7, C17, C18, C26, C27, C42, C43, C44, C45,C24, C29, C31, C33         & 20   & 3.80   \\
08055A102JAT2A      & 478-1328-1-ND            & 1n             & C2,C34, C47                                                               & 10   & 1.26   \\
\bottomrule
\end{tabular}

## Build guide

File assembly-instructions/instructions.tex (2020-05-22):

\documentclass[12pt]{article}
% \documentclass[twoside,12pt]{book}

\usepackage{fontspec}
\usepackage{titling}
\usepackage[labelfont=bf]{caption}
\usepackage{microtype}
\usepackage{siunitx}
\usepackage{enumitem}
\usepackage{booktabs}
\usepackage{geometry}
\geometry{letterpaper}
% \geometry{letterpaper, textwidth=5.5in, textheight=8.5in, marginparsep=7pt, marginparwidth=.6in}
\usepackage[usenames,dvipsnames]{xcolor}
\usepackage{xunicode}
\defaultfontfeatures{Mapping=tex-text}

\usepackage{pdflscape}
\usepackage{pdfpages}

\graphicspath{{figs/}}

\usepackage[xetex, unicode, bookmarks, colorlinks, breaklinks, pdfusetitle]{hyperref}
\hypersetup{linkcolor=MidnightBlue,citecolor=MidnightBlue,filecolor=black,urlcolor=MidnightBlue} % Link colors

% Linux Libertine Font (default)
\setromanfont{Linux Libertine}
\setsansfont{Linux Biolinum}
% \setmonofont[Scale=0.8]{Iosevka}

% \usepackage{sectsty}
% \allsectionsfont{\sffamily}

\renewcommand{\today}{\ifcase\month\or%
  January\or%
  February\or%
  March\or%
  April\or%
  May\or%
  June\or%
  July\or%
  August\or%
  September\or%
  October\or%
  November\or%
  December\fi~%
\number\year}

\usepackage{lipsum}

\newcommand{\kicad}{Ki\textsc{Cad}}

\begin{document}
\title{\textsc{Fifo} Delay Assembly Information}
\author{Alex Striff}
\date{\today}

\begin{titlingpage} %This starts the title page
    \begin{center}
        \vfill\null%
        \begin{Huge} 
            \thetitle\\
        \end{Huge}
        \vspace{0.5cm}
        \begin{Large}
            \theauthor\\
        \end{Large}
        \vfill\null%
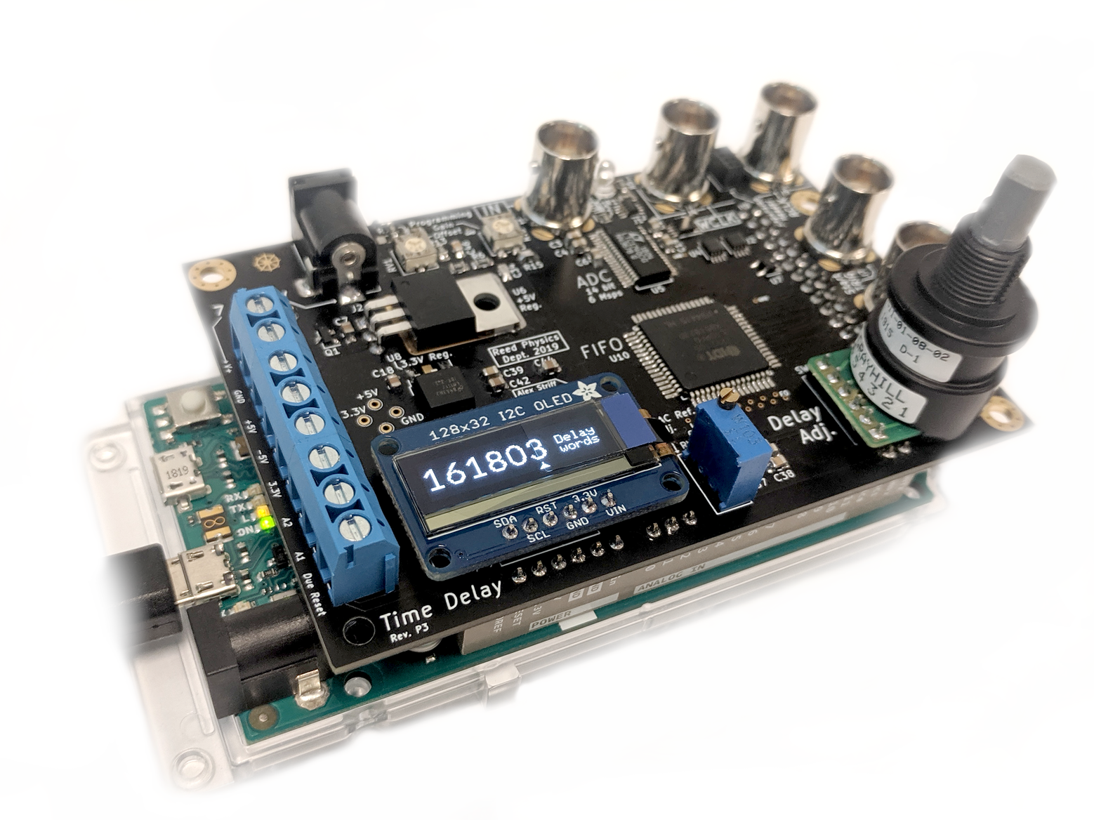
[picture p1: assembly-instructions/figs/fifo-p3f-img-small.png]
        \\
        \vfill\null%
        \begin{large}
        Reed College \\
        Physics Department\\
        \vspace{0.5\baselineskip}
        \thedate%
        \end{large}
        % \vfill\null%
        \tableofcontents%
    \end{center}
\end{titlingpage}

\section{Ordering \textsc{Pcb}s}

Given a complete \href{https://kicad-pcb.org}{\kicad} \textsc{pcb} layout, how
do you order the \textsc{pcb}s?

\subsection{Exporting the \textsc{pcb} files from \kicad}

Circuit board manufacturers expect to receive a \textsc{zip} archive that
contains both the \emph{Gerber} files and \emph{drill} files for a circuit
board. The latest version of the files should exist at
\href{https://github.com/lucasilling/AJP_TimeDelay_Git/tree/master/fifo-p3f/Gerber}{\texttt{/fifo-p3f/Gerber}}
on the \href{https://github.com/lucasilling/AJP_TimeDelay_Git}{GitHub
repository}, but the files may be manually exported from \kicad{} as follows.
With the \textsc{pcb} layout editor open, select \textit{File $\to$ Plot\ldots}
to open the window of Fig.~\ref{fig:gerbers}. Choose an appropriate output
directory and check that all of the correct layers needed for manufacture are
selected, and then select \textit{Generate Drill Files\ldots} to open the window
of Fig.~\ref{fig:mapdrill}. Now set the output directory to be the same as that
for the Gerber files and select the \textit{Generate Drill File} button. You may
also want to generate a map file as a \textsc{pdf} to visually check that the
holes are in reasonable places. Close the drill file window and select
\textit{Plot} in the Gerber file window to generate the Gerber files. You now
should have a directory with several Gerber files for all of the layers and two
drill files (corresponding to plated (\textsc{pth}) and non-plated
(\textsc{npth}) through-holes in the board). Create a \textsc{zip} archive from
the directory of Gerber and drill files. You are now ready to send the files to
a manufacturer.

\begin{figure}
  \centering
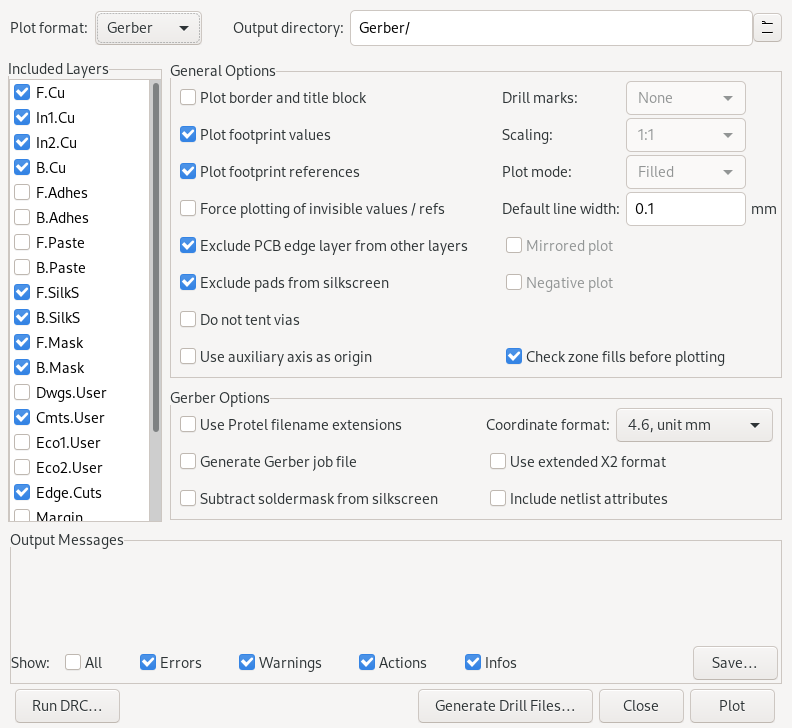
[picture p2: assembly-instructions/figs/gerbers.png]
  
  \caption{Exporting Gerber files.}\label{fig:gerbers}
\end{figure}

\begin{figure}
  \centering
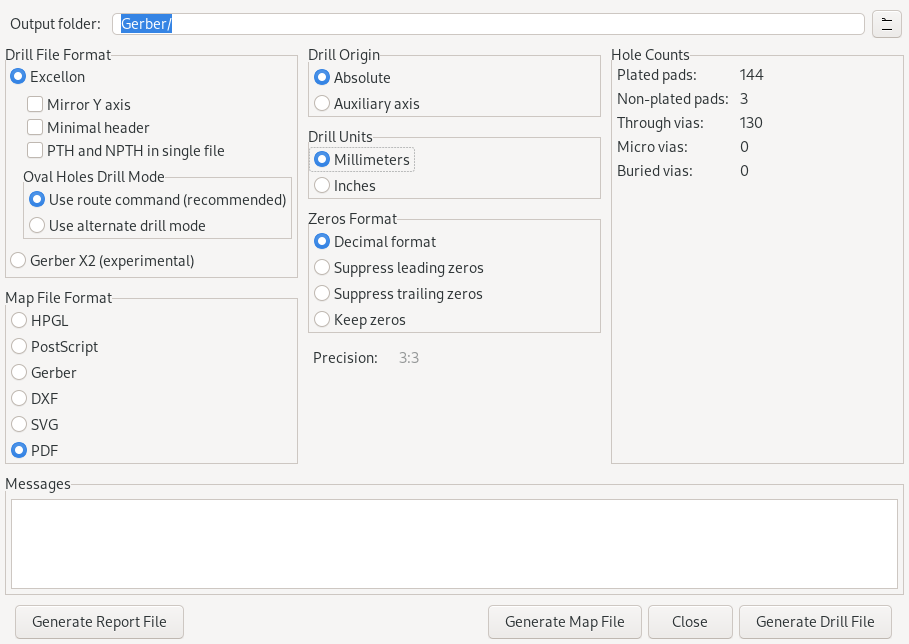
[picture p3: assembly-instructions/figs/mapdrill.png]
  
  \caption{Exporting drill and map files.}\label{fig:mapdrill}
\end{figure}

\subsection{Sending the files to a manufacturer}

There are many prototyping \textsc{pcb} fabrication houses
available,\footnote{To compare prices for given \textsc{pcb} feature sets, see
\url{pcbshopper.com}.} but the one I have used previously is one of the largest,
cheapest, and most popular: \href{https://jlcpcb.com}{\textsc{JlcPcb}}. It is
straightforward to fill out the forms on these order websites, but be sure to
check that their manufacturing tolerances are below what you
request.\footnote{Our board is easily manufacturable by most fabrication
houses.} The turnaround time for these services varies, but is usually quite
fast: about one week or less with \textsc{dhl} shipping.

\section{Ordering Parts}

A complete
\href{https://github.com/lucasilling/AJP_TimeDelay_Git/blob/master/Digikey_BOM.csv}{bill
of materials} (\textsc{bom}) is given on the
\href{https://github.com/lucasilling/AJP_TimeDelay_Git}{GitHub repository}. To
order the parts, one may simply upload the \textsc{bom} file to
\href{https://www.digikey.com/bom}{Digi-Key} (Fig.~\ref{fig:digikey-bom}). The
relevant entries are reproduced in Table~\ref{tab:bom}. This is useful as a
checklist as you solder parts on to the board.

\begin{figure}[hb]
  \centering
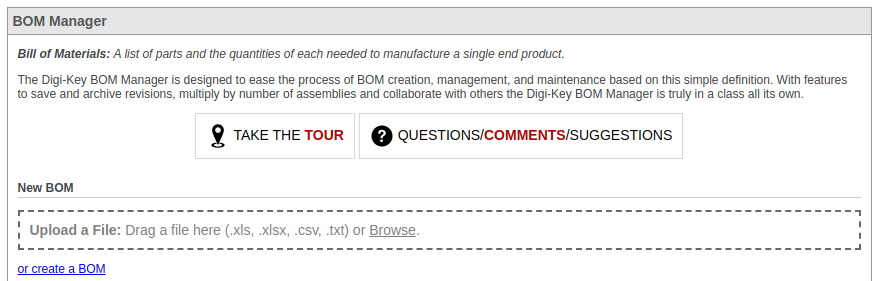
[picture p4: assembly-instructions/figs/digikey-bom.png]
  
  \caption{The Digi-Key \textsc{bom} manager.}\label{fig:digikey-bom}
\end{figure}

\newgeometry{margin=1in}
\begin{landscape}
\begin{table}[ht]
\caption{Bill of materials. Quantities are sometimes rounded up to a multiple of
ten for price breaks.}\label{tab:bom}
\scriptsize
\input{bom.tex}
\end{table}
\end{landscape}
\restoregeometry%

\section{Assembly and Soldering}

Once you have received both parts and boards, you face the task of soldering
them together. If you are unfamiliar with soldering, there are plenty of
resources online, and even surface-mount soldering is easier than it
looks.\footnote{For example,
  \href{https://learn.adafruit.com/adafruit-guide-excellent-soldering/tools}{Adafruit}
covers the basics of through-hole soldering.}
Soldering small \textsc{ic}s with pin pitches of \SI{650}{\um} is simple because
\emph{you} are not doing the fine placement: the surface tension of the solder
is. For that to work, you must be able to control the quantity of solder and
have appropriately prepared surfaces. This is achieved by:
\begin{itemize}
  \item Having good leaded solder with a \emph{small} diameter (less than the
    usual \SI{31}{thou}).
  \item Frequently using a source of flux, such as a flux pen or paste.
\end{itemize}
Mistakes are easily remedied with some solder wick. There is also the
possibility of getting a solder paste stencil with your \textsc{pcb} order and
reflow-soldering the whole board at once.

It is usually a good idea to solder the power supply components first and then
stop to check that the test points give the correct voltages when powered on.
This prevents damage to critical parts like the Arduino or \textsc{fifo} in the
case of an error. Manual continuity checks for densely-packed pins are also a
good idea.

% \begin{landscape}
\includepdf[landscape]{../fifo-p3f/FIFO_P.pdf}
% \end{landscape}

\end{document}

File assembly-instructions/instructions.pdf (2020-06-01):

# Fifo Delay Assembly Information

## Alex Striff

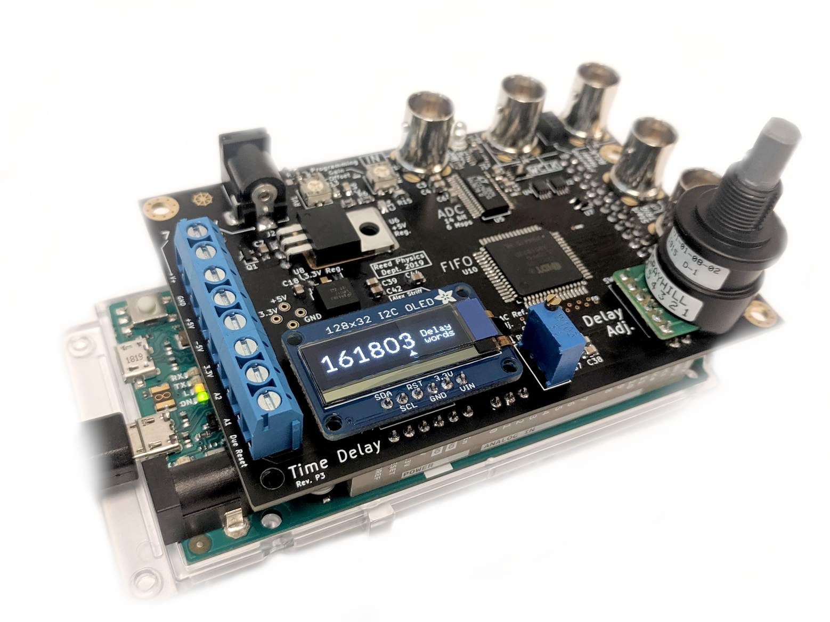
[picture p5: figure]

### Reed College Physics Department May 2020

## Contents

1 Ordering Pcbs | 1
2 Ordering Parts | 1
3 Assembly and Soldering | 6

## 1 Ordering Pcbs

Given a complete KiCad (https://kicad-pcb.org) pcb layout, how do you order the pcbs?

### 1.1 Exporting the pcb files from KiCad

Circuit board manufacturers expect to receive a zip archive that contains both the Gerber files and drill files for a circuit board. The latest version of the files should exist at /fifo-p3f/Gerber (https://github.com/lucasilling/AJP_TimeDelay_Git/tree/master/fifo-p3f/Gerber) on the GitHub repository, (https://github.com/lucasilling/AJP_TimeDelay_Git) but the files may be manually exported from KiCad as follows. With the pcb layout editor open, select File → Plot… to open the window of Fig. 1. Choose an appropriate output directory and check that all of the correct layers needed for manufacture are selected, and then select Generate Drill Files… to open the window of Fig. 2. Now set the output directory to be the same as that for the Gerber files and select the Generate Drill File button. You may also want to generate a map file as a pdf to visually check that the holes are in reasonable places. Close the drill file window and select Plot in the Gerber file window to generate the Gerber files. You now should have a directory with several Gerber files for all of the layers and two drill files (corresponding to plated (pth) and non-plated (npth) through-holes in the board). Create a zip archive from the directory of Gerber and drill files. You are now ready to send the files to a manufacturer.

### 1.2 Sending the files to a manufacturer

There are many prototyping pcb fabrication houses available,¹ but the one I have used previously is one of the largest, cheapest, and most popular: JlcPcb. (https://jlcpcb.com) It is straightforward to fill out the forms on these order websites, but be sure to check that their manufacturing tolerances are below what you request.² The turnaround time for these services varies, but is usually quite fast: about one week or less with dhl shipping.

## 2 Ordering Parts

A complete bill of materials (https://github.com/lucasilling/AJP_TimeDelay_Git/blob/master/Digikey_BOM.csv) (bom) is given on the GitHub repository. (https://github.com/lucasilling/AJP_TimeDelay_Git) To order the parts, one may simply upload the bom file to Digi-Key (https://www.digikey.com/bom) (Fig. 3). The relevant entries are repro-duced in Table 1. This is useful as a checklist as you solder parts on to the board.

1To compare prices for given pcb feature sets, see pcbshopper.com.
2Our board is easily manufacturable by most fabrication houses.

1


Figure 1: Exporting Gerber files.

2


Figure 2: Exporting drill and map files.

3

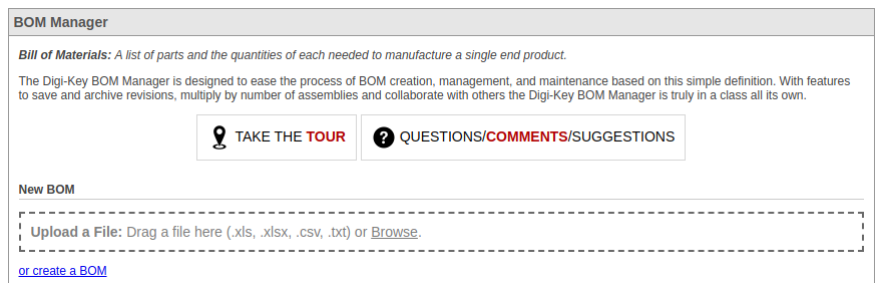
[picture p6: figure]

Figure 3: The Digi-Key bom manager.

4

Table 1: Bill of materials. Quantities are sometimes rounded up to a multiple of ten for price breaks.

Manufacturer Part Number | Digi-Key Part Number | Customer Reference | Reference Designator | Quantity | Extended Price
LM2940CT-5.0/NOPB | LM2940CT-5.0/NOPB-ND | | U6 | 1 | 1.53
LM2776DBVR | 296-43957-1-ND | | U15 | 1 | 1.02
AD7840ARSZ | AD7840ARSZ-ND | | U13 | 1 | 33.39
72V2105L10PFG | 800-1511-ND | | U10 | 1 | 131.65
LTC1740CG#PBF | LTC1740CG#PBF-ND | | U5 | 1 | 41.67
SN74LVC2G157DCTR | 296-13266-1-ND | | U2 | 3 | 1.44
4440 | 1528-4440-ND | 128x32 OLED | U11 | 1 | 12.50
TS12A12511DCNR | 296-27523-1-ND | | U1 | 1 | 1.45
LM4041DYM3-ADJ-TR | 576-2573-1-ND | | U14 | 1 | 0.29
SN74LVC1G04DBVR | 296-11599-1-ND | | U7 | 1 | 0.32
SN74LVC1G08DBVR | 296-11601-1-ND | | U12 | 1 | 0.26
LM1117IDTX-3.3/NOPB | LM1117IDTX-3.3/NOPBCT-ND | | U8 | 1 | 1.44
TL082CDR | 296-1284-1-ND | | U16 | 1 | 0.41
A000062 | 1050-1049-ND | | U9 | 1 | 37.40
PRPC002SAAN-RC | S1011EC-02-ND | Board to board | U9 | 2 | 0.16
54102-S08-18 | 609-5600-ND | Board to board | U9 | 1 | 1.45
PRPC003SAAN-RC | S1011EC-03-ND | Board to board | U9 | 1 | 0.12
PRPC006SAAN-RC | S1011EC-06-ND | Board to board | U9 | 1 | 0.19
LPPB042CFFN-RC | S9009E-04-ND | Board to board | U9 | 1 | 1.05
DMP3099L-7 | DMP3099L-7DICT-ND | | Q1 | 1 | 0.33
151033RS03000 | 732-5013-ND | | D1 | 1 | 0.17
61C11-01-08-02 | GH6102-ND | | SW1 | 1 | 25.77
5-1634503-1 | A97581-ND | | J1, J4, J5, J7, J8 | 5 | 11.25
PJ-002A | CP-002A-ND | | J2 | 1 | 0.60
OSTTC082162 | ED2615-ND | | J3 | 1 | 1.72
TS53YL102MR10 | TS53YL-1.0KCT-ND | | RV1, RV3 | 2 | 3.74
3296W-1-103LF | 3296W-103LF-ND | | RV2 | 1 | 2.41
RC0805FR-0749R9L | 311-49.9CRCT-ND | | R1, R3, R4, R19 | 4 | 0.40
RC0805FR-0722RL | 311-22.0CRCT-ND | | R2, R6, R20 | 3 | 0.30
RC0805FR-07220RL | 311-220CRCT-ND | | R5 | 1 | 0.10
RC0805FR-075K1L | 311-5.10KCRCT-ND | | R7, R9, R10, R11, R13, R16, R17, R18 | 10 | 0.40
RC0805FR-071K1L | 311-1.10KCRCT-ND | | R8, R14 | 2 | 0.20
RC0805FR-073K9L | 311-3.90KCRCT-ND | | R15 | 1 | 0.10
RC0805FR-074K3L | 311-4.30KCRCT-ND | | R12 | 1 | 0.10
RC0805JR-070RL | 311-0.0ARCT-ND | Jumpers | | 10 | 0.35
08055C104KAT2A | 478-1395-1-ND | 0u1 | C8, C9, C10, C15, C16, C22, C46,C23, C28, C30, C32, C37, C38 | 20 | 1.66
08053C105KAT2A | 478-5030-1-ND | 1u | C1, C3, C4, C6, C19, C20, C40, C41,C11, C12, C13, C14, C21, C25, C35, C39 | 20 | 3.52
CL21A106KAYNNNE | 1276-2891-1-ND | 10u | C5, C7, C17, C18, C26, C27, C42, C43, C44, C45,C24, C29, C31, C33 | 20 | 3.80
08055A102JAT2A | 478-1328-1-ND | 1n | C2,C34, C47 | 10 | 1.26

5

## 3 Assembly and Soldering

Once you have received both parts and boards, you face the task of soldering them to-gether. If you are unfamiliar with soldering, there are plenty of resources online, and even surface-mount soldering is easier than it looks.³ Soldering small ics with pin pitches of 650 µm is simple because you are not doing the fine placement: the surface tension of the solder is. For that to work, you must be able to control the quantity of solder and have appropriately prepared surfaces. This is achieved by:

- Having good leaded solder with a small diameter (less than the usual 31 thou).
- Frequently using a source of flux, such as a flux pen or paste.

Mistakes are easily remedied with some solder wick. There is also the possibility of get-ting a solder paste stencil with your pcb order and reflow-soldering the whole board at once.
It is usually a good idea to solder the power supply components first and then stop to check that the test points give the correct voltages when powered on. This prevents damage to critical parts like the Arduino or fifo in the case of an error. Manual continuity checks for densely-packed pins are also a good idea.

3For example, Adafruit (https://learn.adafruit.com/adafruit-guide-excellent-soldering/tools) covers the basics of through-hole soldering.

6

10u GNDA GNDA | GNDA | GNDA | GND

# 0u1 GNDA GND

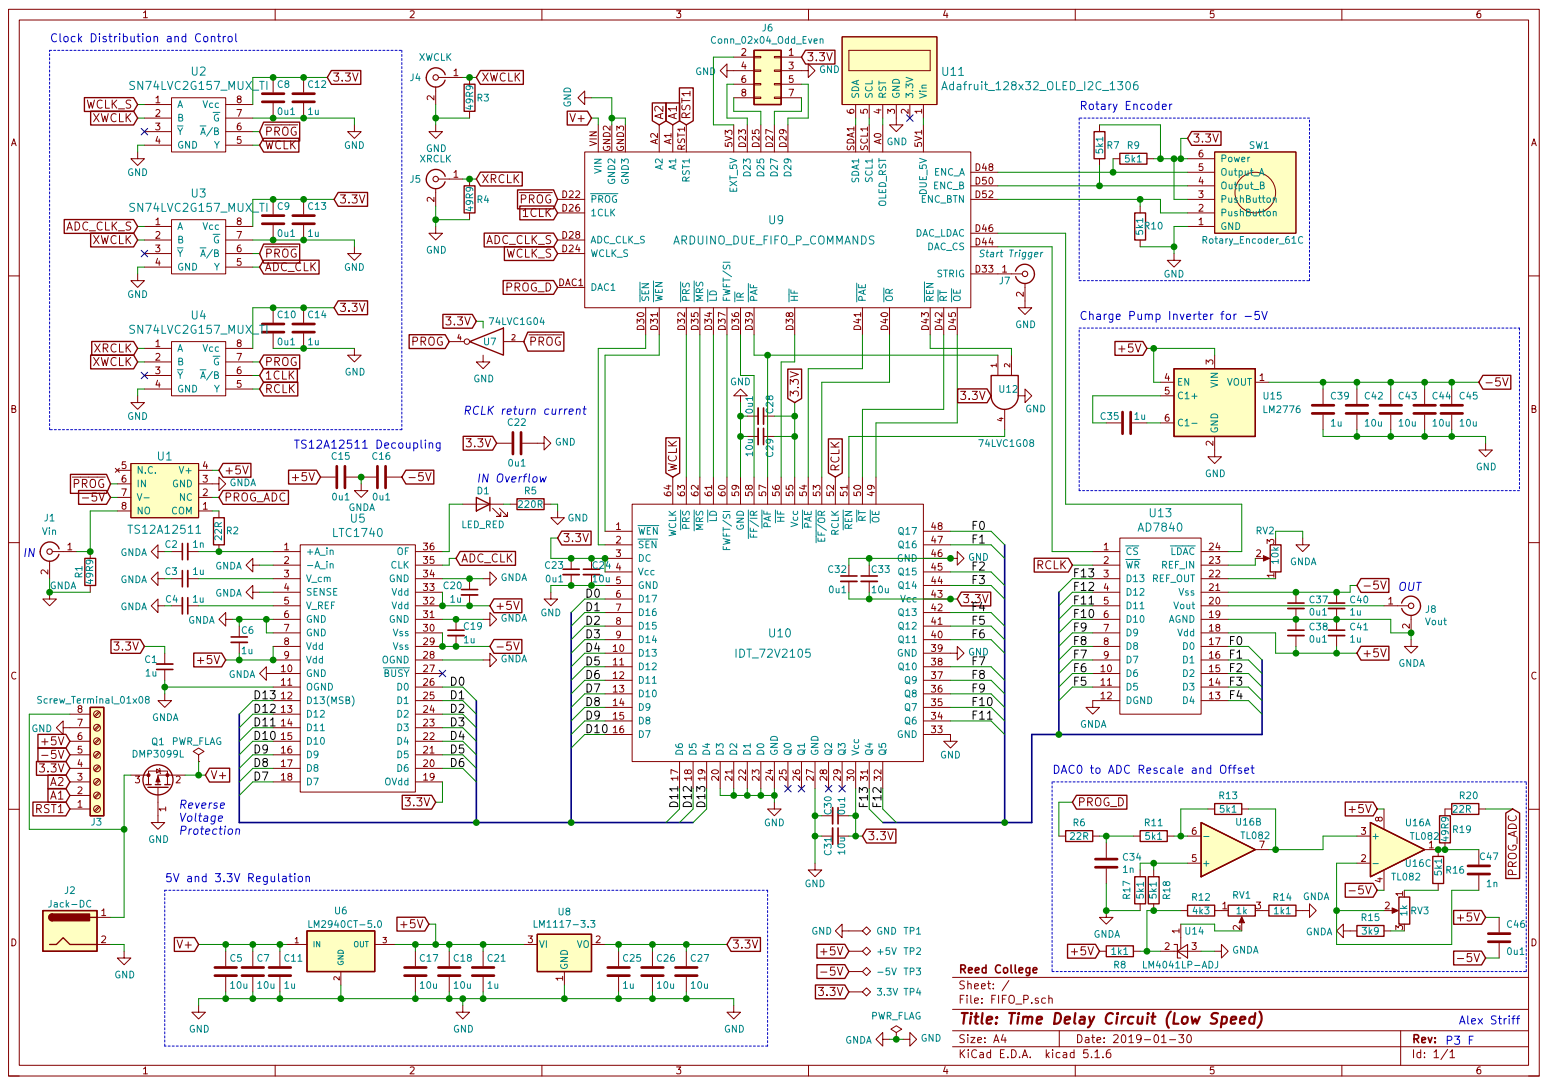
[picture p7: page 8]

DAC0 to ADC Rescale and Offset

File: FIFO_P.sch Sheet: / Reed College

Id: 1/1 Title: Time Delay Circuit (Low Speed)

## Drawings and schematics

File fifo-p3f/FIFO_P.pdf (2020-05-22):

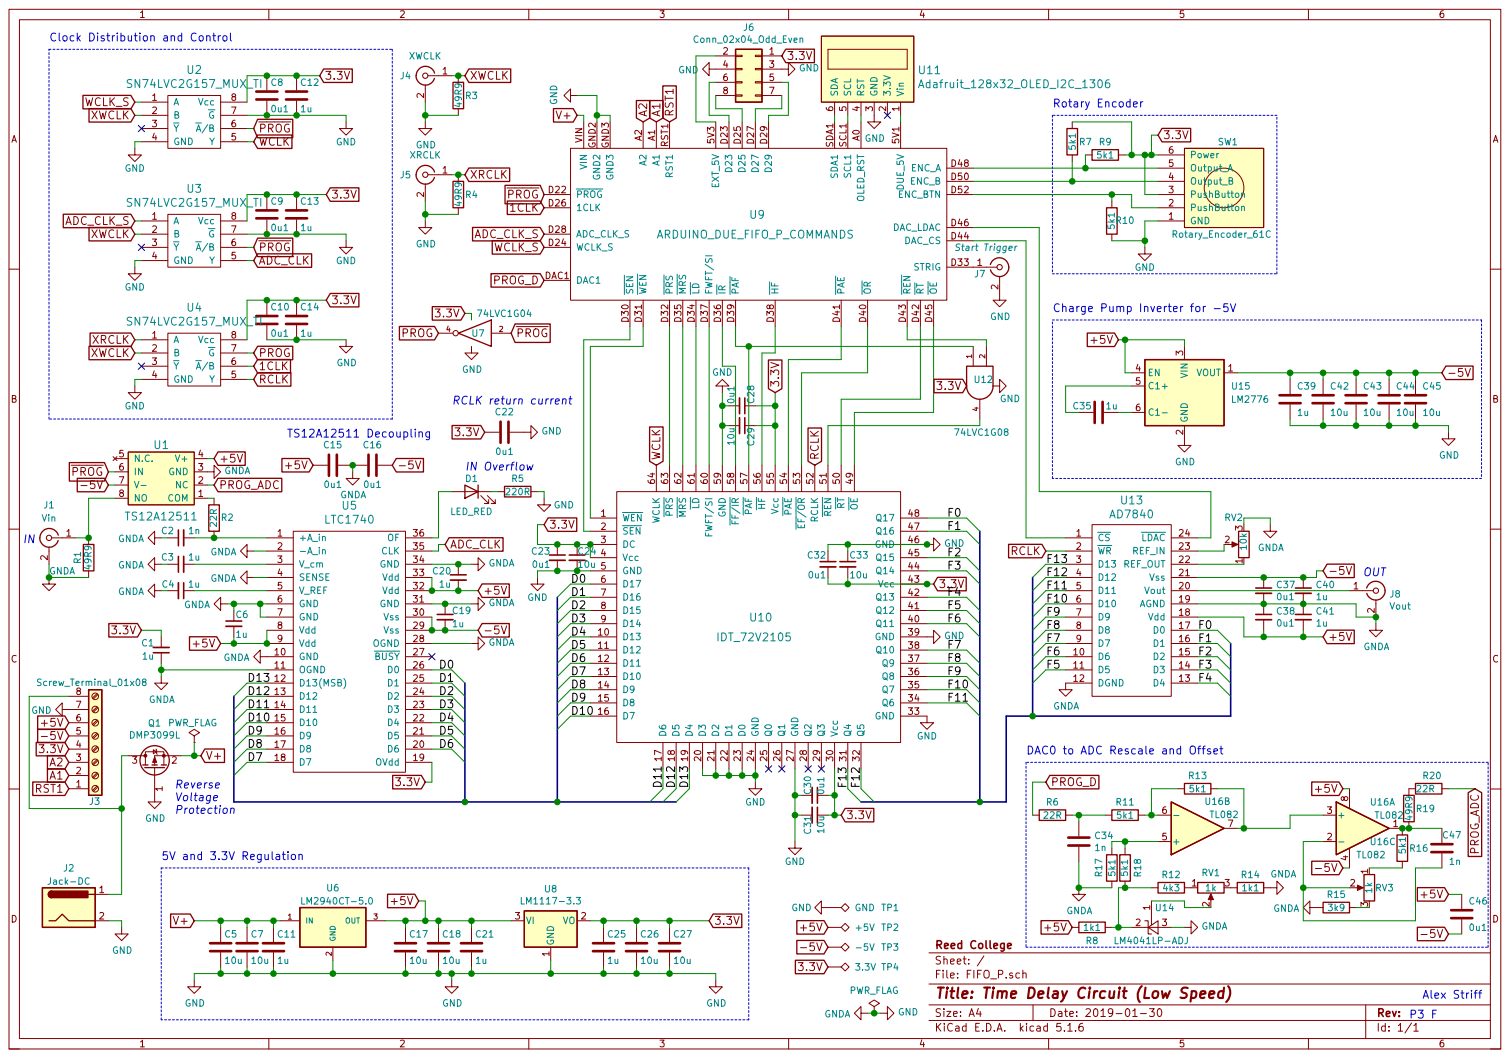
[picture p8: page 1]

6 U11Adafruit_128x32_OLED_I2C_1306 GND 1 PushButton 2 PushButton 3 Output_B 4 Output_A 5 Power 6 SW1 Rotary_Encoder_61C WEN 1 D13 10 D12 11 D11 12 D10 13 D9 14 D8 15 D7 16 D6 17 D5 18 D4 19 SEN 2 D3 20 D2 21 D1 22 D0 23 GND 24 Q0 25 Q1 26 GND 27 Q2 28 Q3 29 DC 3 Vcc 30 Q4 31 Q5 32 GND 33 Q6 34 Q7 35 Q8 36 Q9 37 Q10 38 GND 39 Vcc 4 Q11 40 Q12 41 Q13 42 Vcc 43 Q14 44 Q15 45 GND 46 Q16 47 Q17 48 OE 49 GND 5 RT 50 REN 51 RCLK 52 EF/OR 53 PAE 54 Vcc 55 HF 56 PAF 57 FF/IR 58 GND 59 D17 6 FWFT/SI 60 LD 61 MRS 62 PRS 63 WCLK 64 D16 7 D15 8 D14 9 U10

DAC0 to ADC Rescale and Offset

File: FIFO_P.sch Sheet: / Reed College

Id: 1/1 Title: Time Delay Circuit (Low Speed)

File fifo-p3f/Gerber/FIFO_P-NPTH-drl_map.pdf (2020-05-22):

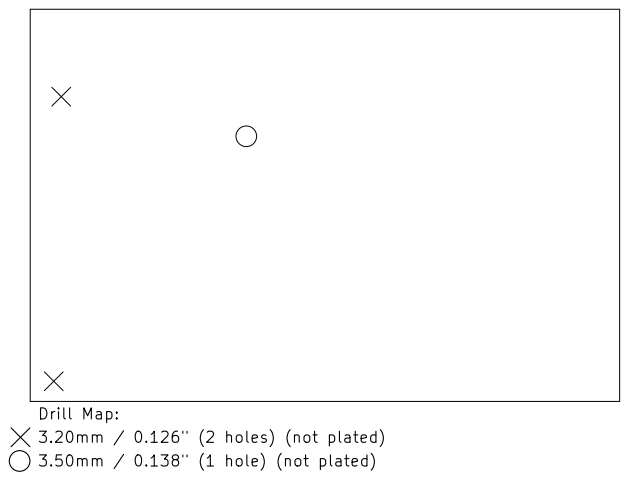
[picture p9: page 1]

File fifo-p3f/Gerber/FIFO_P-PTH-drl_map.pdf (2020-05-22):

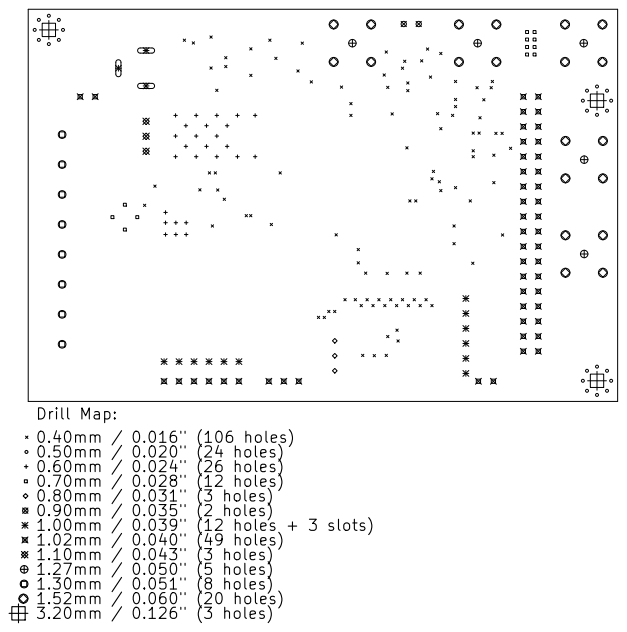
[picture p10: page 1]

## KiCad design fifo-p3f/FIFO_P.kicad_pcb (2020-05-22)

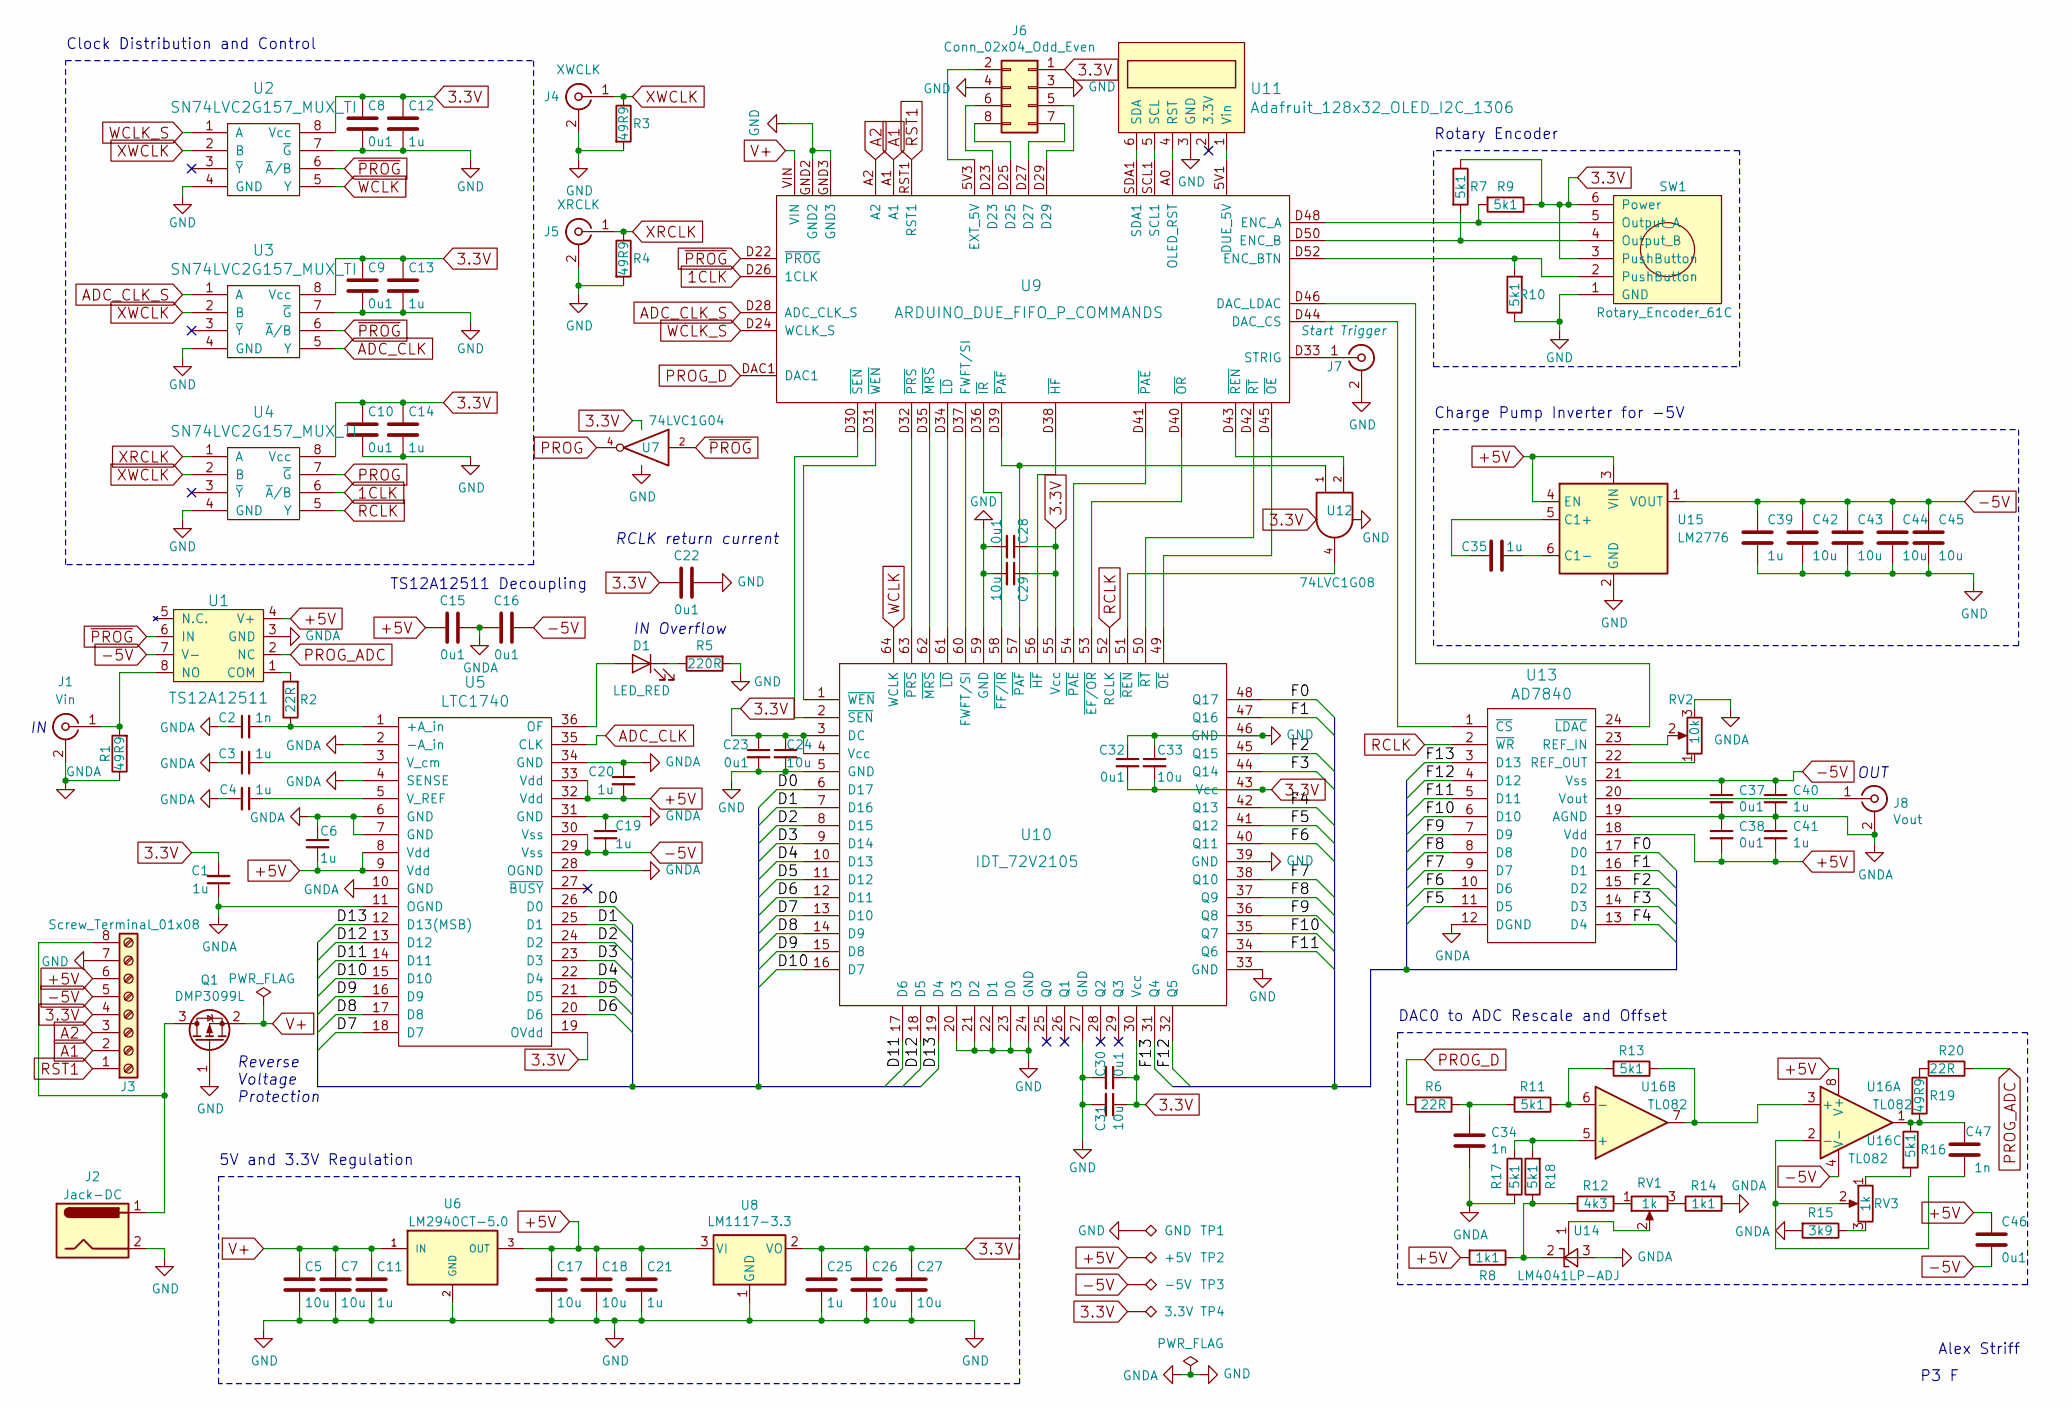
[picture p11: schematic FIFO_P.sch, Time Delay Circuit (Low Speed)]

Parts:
C1, C3, C4, C6, C11, C12, C13, C14, C19, C20, C21, C25, C35, C39, C40, C41: 1u; C_0805_2012Metric_Pad1.15x1.40mm_HandSolder
C2, C34, C47: 1n; C_0805_2012Metric_Pad1.15x1.40mm_HandSolder
C5, C7, C17, C18, C24, C26, C27, C29, C31, C33, C42, C43, C44, C45: 10u; C_0805_2012Metric_Pad1.15x1.40mm_HandSolder
C8, C9, C10, C15, C16, C22, C23, C28, C30, C32, C37, C38, C46: 0u1; C_0805_2012Metric_Pad1.15x1.40mm_HandSolder
D1: LED_RED; LED_D3.0mm
J1: Vin; BNC_TEConnectivity_1478204_Vertical
J2: Jack-DC; BarrelJack_Horizontal
J3: Screw_Terminal_01x08; TerminalBlock_Phoenix_MKDS-3-8-5.08_1x08_P5.08mm_Horizontal
J4: XWCLK; BNC_TEConnectivity_1478204_Vertical
J5: XRCLK; BNC_TEConnectivity_1478204_Vertical
J6: Conn_02x04_Odd_Even; PinSocket_2x04_P1.27mm_Vertical
J7: Start Trigger; BNC_TEConnectivity_1478204_Vertical
J8: Vout; BNC_TEConnectivity_1478204_Vertical
Q1: DMP3099L; SOT-23
R1, R3, R4, R19: 49R9; R_0805_2012Metric_Pad1.15x1.40mm_HandSolder
R2, R6, R20: 22R; R_0805_2012Metric_Pad1.15x1.40mm_HandSolder
R5: 220R; R_0805_2012Metric_Pad1.15x1.40mm_HandSolder
R7, R9, R10, R11, R13, R16, R17, R18: 5k1; R_0805_2012Metric_Pad1.15x1.40mm_HandSolder
R8, R14: 1k1; R_0805_2012Metric_Pad1.15x1.40mm_HandSolder
R12: 4k3; R_0805_2012Metric_Pad1.15x1.40mm_HandSolder
R15: 3k9; R_0805_2012Metric_Pad1.15x1.40mm_HandSolder
RV1, RV3: 1k; Potentiometer_Vishay_TS53YL_Vertical
RV2: 10k; Potentiometer_Bourns_3296W_Vertical
SW1: Rotary_Encoder_61C
TP1: GND; Test_Pin
TP2: +5V; Test_Pin
TP3: -5V; Test_Pin
TP4: 3.3V; Test_Pin
U1: TS12A12511; SOT-23-8_Handsoldering
U2, U3, U4: SN74LVC2G157_MUX_TI; SSOP-8_2.95x2.8mm_P0.65mm
U5: LTC1740; SSOP-36_5.3mm_Pitch0.65mm
U6: LM2940CT-5.0; TO-220-3_Horizontal_TabDown
U7: 74LVC1G04; SOT-23-5_HandSoldering
U8: LM1117-3.3; TO-252-3_TabPin2
U9: ARDUINO_DUE_FIFO_P_COMMANDS; Arduino_Due_Selected_Pins
U10: IDT_72V2105; LQFP-64_14x14mm_P0.8mm_HandSolder
U11: Adafruit_128x32_OLED_I2C_1306
U12: 74LVC1G08; SOT-23-5_HandSoldering
U13: AD7840; SSOP-24_5.3x8.2mm_P0.65mm
U14: LM4041LP-ADJ; SOT-23_Handsoldering
U15: LM2776; SOT-23-6
U16: TL082; SOIC-8_3.9x4.9mm_P1.27mm

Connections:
1CLK: U4.6 (~A~/B~), U9.D26 (1CLK)
3.3V: C1.2, C8.1, C9.1, C10.1, C12.1, C13.1, C14.1, C22.1, C23.1, C24.1, C25.1, C26.1, C27.1, C28.1, C29.1, C30.1, C31.1, C32.2, C33.2, J3.4, J6.1, R7.1, R9.1, SW1.3 (PushButton), SW1.6 (Power), TP4.1, U2.8 (Vcc), U3.8 (Vcc), U4.8 (Vcc), U5.19 (OVdd), U7.5 (VCC), U8.2 (VO), U10.3 (DC), U10.4 (Vcc), U10.30 (Vcc), U10.43 (Vcc), U10.55 (Vcc), U12.5 (VCC)
+5V: C6.2, C15.1, C17.1, C18.1, C20.2, C21.1, C38.2, C41.2, C46.1, J3.6, R8.2, TP2.1, U1.4 (V+), U5.8 (Vdd), U5.9 (Vdd), U5.32 (Vdd), U5.33 (Vdd), U6.3 (OUT), U8.3 (VI), U13.18 (Vdd), U15.3 (VIN), U15.4 (EN), U16.8 (V+)
-5V: C16.2, C19.2, C37.1, C39.1, C40.1, C42.1, C43.1, C44.1, C45.1, C46.2, J3.5, TP3.1, U1.7 (V-), U5.29 (Vss), U5.30 (Vss), U13.21 (Vss), U15.1 (VOUT), U16.4 (V-)
/D0: U5.26 (D0), U10.6 (D17)
/D1: U5.25 (D1), U10.7 (D16)
/D2: U5.24 (D2), U10.8 (D15)
/D3: U5.23 (D3), U10.9 (D14)
/D4: U5.22 (D4), U10.10 (D13)
/D5: U5.21 (D5), U10.11 (D12)
/D6: U5.20 (D6), U10.12 (D11)
/D7: U5.18 (D7), U10.13 (D10)
/D8: U5.17 (D8), U10.14 (D9)
/D9: U5.16 (D9), U10.15 (D8)
/D10: U5.15 (D10), U10.16 (D7)
/D11: U5.14 (D11), U10.17 (D6)
/D12: U5.13 (D12), U10.18 (D5)
/D13: U5.12 (D13(MSB)), U10.19 (D4)
/F0: U10.48 (Q17), U13.17 (D0)
/F1: U10.47 (Q16), U13.16 (D1)
/F2: U10.45 (Q15), U13.15 (D2)
/F3: U10.44 (Q14), U13.14 (D3)
/F4: U10.42 (Q13), U13.13 (D4)
/F5: U10.41 (Q12), U13.11 (D5)
/F6: U10.40 (Q11), U13.10 (D6)
/F7: U10.38 (Q10), U13.9 (D7)
/F8: U10.37 (Q9), U13.8 (D8)
/F9: U10.36 (Q8), U13.7 (D9)
/F10: U10.35 (Q7), U13.6 (D10)
/F11: U10.34 (Q6), U13.5 (D11)
/F12: U10.32 (Q5), U13.4 (D12)
/F13: U10.31 (Q4), U13.3 (D13)
A1: J3.2, U9.A1
A2: J3.3, U9.A2
ADC_CLK: U3.5 (Y), U5.35 (CLK)
ADC_CLK_S: U3.1 (A), U9.D28 (ADC_CLK_S)
GND: C1.1, C2.1, C3.1, C4.2, C5.2, C6.1, C7.2, C8.2, C9.2, C10.2, C11.2, C12.2, C13.2, C14.2, C15.2, C16.1, C17.2, C18.2, C19.1, C20.1, C21.2, C22.2, C23.2, C24.2, C25.2, C26.2, C27.2, C28.2, C29.2, C30.2, C31.2, C32.1, C33.1, C34.2, C37.2, C38.1, C39.2, C40.2, C41.1, C42.2, C43.2, C44.2, C45.2, J1.2 (Ext), J2.2, J3.7, J4.2 (Ext), J5.2 (Ext), J6.3, J6.4, J7.2 (Ext), J8.2 (Ext), Q1.1 (G), R1.1, R3.2, R4.2, R5.2, R10.1, R14.2, R15.2, R17.2, RV2.3, SW1.1 (GND), TP1.1, U1.3 (GND), U2.4 (GND), U2.7 (~G), U3.4 (GND), U3.7 (~G), U4.4 (GND), U5.2 (-A_in), U5.4 (SENSE), U5.6 (GND), U5.7 (GND), U5.10 (GND), U5.11 (OGND), U5.28 (OGND), U5.31 (GND), U5.34 (GND), U6.2 (GND), U7.3 (GND), U8.1 (GND), U9.GND2, U9.GND3, U10.5 (GND), U10.20 (D3), U10.21 (D2), U10.22 (D1), U10.23 (D0), U10.24 (GND), U10.27 (GND), U10.33 (GND), U10.39 (GND), U10.46 (GND), U10.59 (GND), U11.3 (GND), U12.3 (GND), U13.12 (DGND), U13.19 (AGND), U14.3 (A), U15.2 (GND)
unnamed: C2.2, R2.1, U5.1 (+A_in)
unnamed: C3.2, U5.3 (V_cm)
unnamed: C4.1, U5.5 (V_REF)
unnamed: C34.1, R6.1, R11.2
unnamed: C35.1, U15.6 (C1-)
unnamed: C35.2, U15.5 (C1+)
unnamed: C47.1, R16.1, R19.2, U16.1
unnamed: C47.2, RV3.2, U16.2 (-)
unnamed: D1.1 (K), R5.1
unnamed: D1.2 (A), U5.36 (OF)
unnamed: J1.1 (In), R1.2, U1.8 (NO)
unnamed: J2.1, J3.8, Q1.3 (D)
unnamed: J6.2, U9.5V3 (EXT_5V)
unnamed: J6.5, U9.D29
unnamed: J6.6, U9.D23
unnamed: J6.7, U9.D27
unnamed: J6.8, U9.D25
unnamed: J7.1 (In), U9.D33 (STRIG)
unnamed: J8.1 (In), U13.20 (Vout)
unnamed: R2.2, U1.1 (COM)
unnamed: R7.2, SW1.4 (Output_B), U9.D50 (ENC_B)
unnamed: R9.2, SW1.5 (Output_A), U9.D48 (ENC_A)
unnamed: R10.2, SW1.2 (PushButton), U9.D52 (ENC_BTN)
unnamed: R11.1, R13.2, U16.6 (-)
unnamed: R8.1, R12.1, R18.1, U14.2 (K)
unnamed: R12.2, RV1.1
unnamed: R13.1, U16.3 (+), U16.7
unnamed: R14.1, RV1.3
unnamed: R15.1, RV3.3
unnamed: R16.2, RV3.1
unnamed: R17.1, R18.2, U16.5 (+)
unnamed: R19.1, R20.2
unnamed: RV1.2, U14.1 (FB)
unnamed: RV2.1, U13.22 (REF_OUT)
unnamed: RV2.2, U13.23 (REF_IN)
unnamed: U9.D31 (~WEN), U10.1 (~WEN)
unnamed: U9.D30 (~SEN), U10.2 (~SEN)
unnamed: U9.D45 (~OE), U10.49 (~OE)
unnamed: U9.D42 (~RT), U10.50 (~RT)
unnamed: U10.51 (~REN), U12.4
unnamed: U9.D40 (~OR), U10.53 (~EF/OR)
unnamed: U9.D41 (~PAE), U10.54 (~PAE)
unnamed: U9.D38 (~HF), U10.56 (~HF)
unnamed: U9.D39 (~PAF), U10.57 (~PAF), U12.1
unnamed: U9.D36 (~IR), U10.58 (~FF/IR)
unnamed: U9.D37 (FWFT/SI), U10.60 (FWFT/SI)
unnamed: U9.D34 (~LD), U10.61 (~LD)
unnamed: U9.D35 (~MRS), U10.62 (~MRS)
unnamed: U9.D32 (~PRS), U10.63 (~PRS)
unnamed: U9.5V1 (DUE_5V), U11.1 (Vin)
unnamed: U9.A0 (OLED_RST), U11.4 (RST)
unnamed: U9.SCL1, U11.5 (SCL)
unnamed: U9.SDA1, U11.6 (SDA)
unnamed: U9.D43 (~REN), U12.2
unnamed: U9.D44 (DAC_CS), U13.1 (~CS)
unnamed: U9.D46 (DAC_LDAC), U13.24 (~LDAC)
PROG: U4.7 (~G), U7.4
PROG_ADC: R20.1, U1.2 (NC)
PROG_D: R6.2, U9.DAC1
RCLK: U4.5 (Y), U10.52 (RCLK), U13.2 (~WR)
RST1: J3.1, U9.RST1
V+: C5.1, C7.1, C11.1, Q1.2 (S), U6.1 (IN), U9.VIN
WCLK: U2.5 (Y), U10.64 (WCLK)
WCLK_S: U2.1 (A), U9.D24 (WCLK_S)
XRCLK: J5.1 (In), R4.1, U4.1 (A)
XWCLK: J4.1 (In), R3.1, U2.2 (B), U3.2 (B), U4.2 (B)
~PROG: U1.6 (IN), U2.6 (~A~/B~), U3.6 (~A~/B~), U7.2, U9.D22 (~PROG)

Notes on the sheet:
Rotary Encoder
P3 F
5V and 3.3V Regulation
Clock Distribution and Control
Charge Pump Inverter for -5V
DAC0 to ADC Rescale and Offset
TS12A12511 Decoupling
Reverse Voltage Protection
IN Overflow
OUT
RCLK return current
Alex Striff

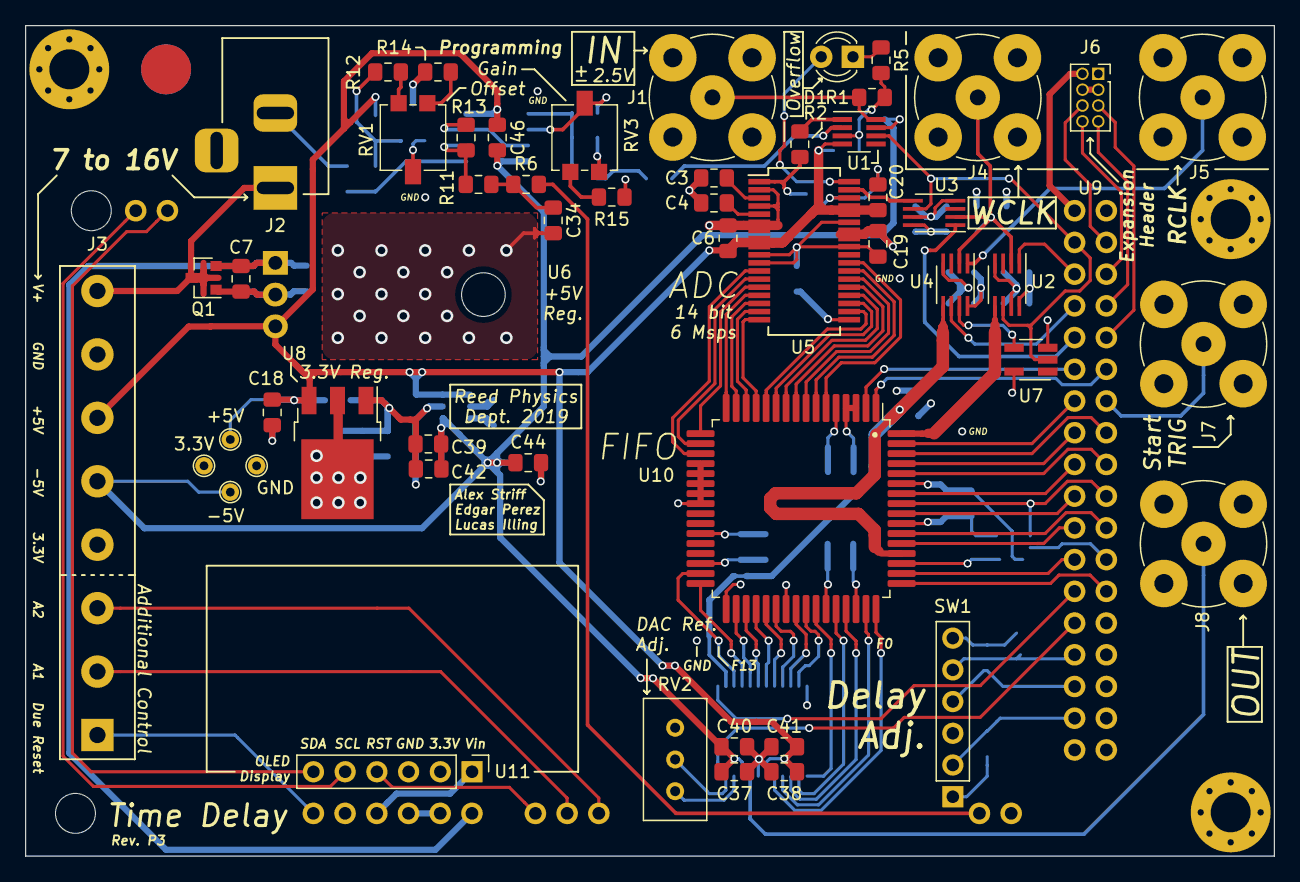
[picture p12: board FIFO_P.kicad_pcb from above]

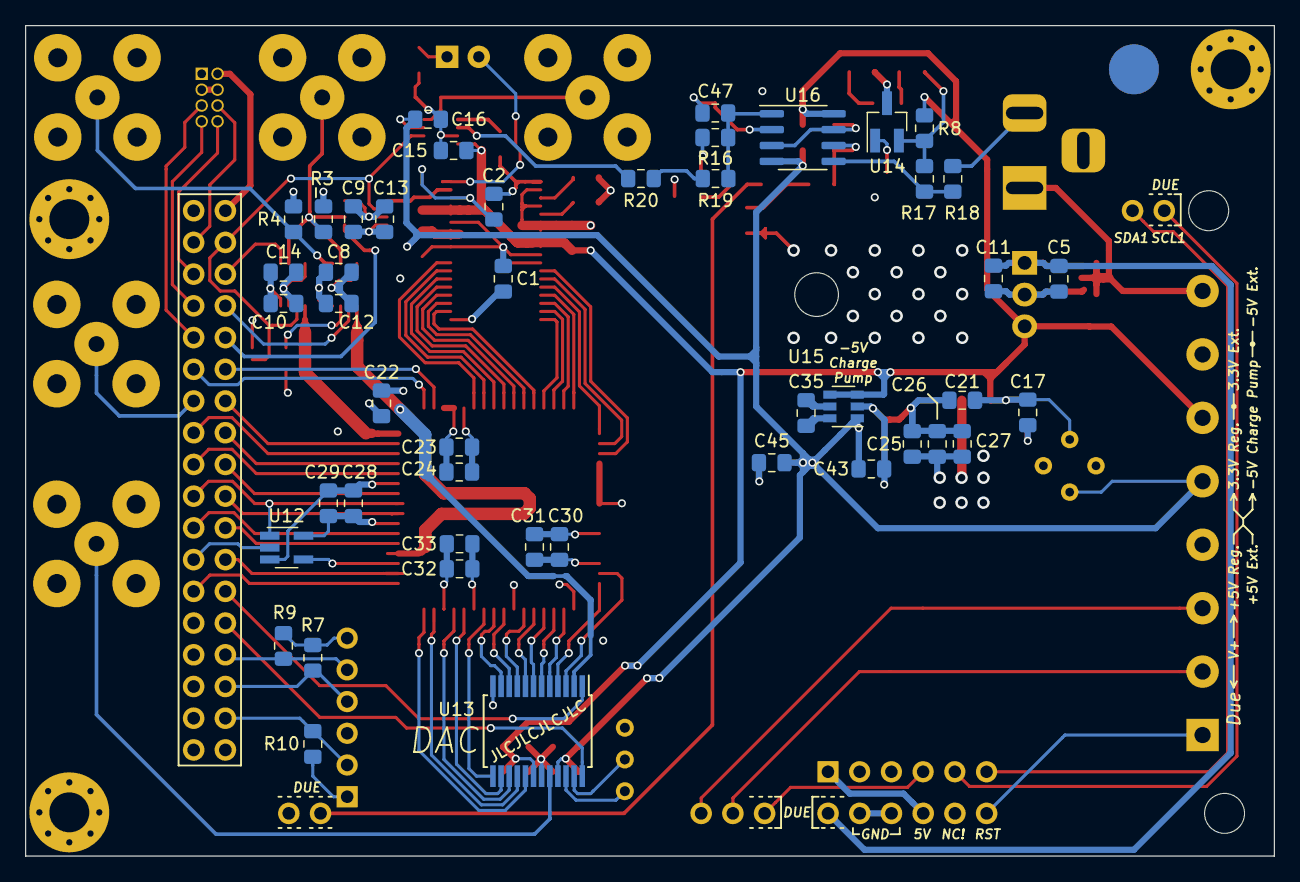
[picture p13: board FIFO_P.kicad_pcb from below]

Board: 4 copper layers, 100.0 x 66.5 mm, 100 parts (46 on the bottom side), 104 nets.

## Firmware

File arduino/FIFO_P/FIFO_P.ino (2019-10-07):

/*******************************************************************************
 * Time Delay Device Arduino Control
 * Edgar Perez and Alex Striff
 * Reed College Physics Department
 *
 * For more information, contact Lucas Illing <illing@reed.edu>.
 *
 * Version  Date        Author       Changes
 * -------  ----------  -----------  -------------------------------------------
 * v1.0     2016-12-15  Edgar Perez  Prototype completed.
 * v2.0     2019-07-XX  Alex Striff  Modified for publication board.
 *
 ******************************************************************************/

// Code options (feature selection)
#define SCREEN   // Uncomment to enable screen output
#define SCONTROL // Uncomment for serial control and logging
#define HISTORY  // Uncomment for FIFO initial state programming (req: SCONTROL)
#define DEBUG    // Uncomment for serial debug output

#if defined(HISTORY) && defined(SCONTROL)
#define HIST
#include <CRC32.h>
#endif

#ifdef SCREEN
#include <Wire.h>
#include <Adafruit_GFX.h>
#include <Adafruit_SSD1306.h>
// #include <Fonts/FreeSans9pt7b.h>
#include "lato24.h"

#define DIGIT_FONT  &Lato_Regular_24 // 24 px high
#define TEXT_FONT   NULL  // 8 px high, NULL for default font in Adafruit GFX

extern TwoWire Wire1; // Use second I2C pins on the Due

#define SCREEN_WIDTH 128 // OLED display width, in pixels
#define SCREEN_HEIGHT 32 // OLED display height, in pixels
#define OLED_RESET    A0 // Reset pin (or -1 if sharing Arduino reset pin)
Adafruit_SSD1306 display(SCREEN_WIDTH, SCREEN_HEIGHT, &Wire1, OLED_RESET);
boolean screen = true;
boolean draw   = true;
char s_digits[16];

enum menu_mode {
    MENU = 0, // Main menu
    DELAY,    // Adjust the word count using the rotary encoder
    FIFO,     // Show FIFO status
    MENU_MODES,
} menu_mode = DELAY;

const PROGMEM char menu_names[][16] = {
    "Menu",
    "Delay",
    "FIFO",
};

uint32_t menu_pos = MENU + 1;
int menu_press = 0;

// Double-press parameters
int dpress = 0;
long dpress_delay = 100L;
long dpress_time = 0L;

// Repeated drawing parameters (in ms)
long last_update = 0L;
long update_interval = 100L; 

#endif // SCREEN

typedef const uint8_t pin;

typedef struct {
    pin p;                      // The pin that the button is connected to.
    long debounce_delay;        // The delay (ms) for debouncing a button press.
    int state;                  // The current state of the button.
    int last_state;             // The last state of the button.
    long last_debounce_time;    // The last debounce time for the button.
} button;

typedef struct {
    pin a;          // Output A
    pin b;          // Output B
    button btn;     // Button (knob of encoder)
} rotary_encoder;

// FIFO word limits
// min_words = 1 or 2 give the same delay.
// min_words = 3 is off-by-one depending upon the clock.
// FIFO words:  0        1  2  3     4   5  ...
// Delay words: invalid  8  8  9,10  11  12 ...
const uint32_t min_words  = 4; // FIFO flags
const uint32_t max_words  = 262144; // FIFO flags
const uint32_t off_words  = 3 + 2 + 2; // ADC + DAC + FIFO.
const uint32_t init_words = 100; // FIFO + offset (user-visible)

#ifdef HIST
// History programming buffer
#define HBUF_SIZE   16 // Make hist relatively large, given SRAM limitations
byte hist[HBUF_SIZE];  // Holds (HBUF_SIZE / 2) code words (uint16_t)
#endif // HIST

// Rotary encoder pin mapping
rotary_encoder enc = {
    .a   = 48, // ENC_A pin
    .b   = 50, // ENC_B pin
    .btn = {
        .p = 52, // ENC_BTN pin
        .debounce_delay = 50,
        .state = 0,
        .last_state = 0,
        .last_debounce_time = 0
    }
};

uint32_t words; // The number of delay words for the FIFO
uint32_t words_digit = 0;

int32_t  count_min = min_words;
int32_t  count_max = max_words;
int32_t  count_mul = 1000;

// FIFO pin mappings:
// Active LOW unless stated otherwise
pin RT    = 42;
pin OE    = 45;
pin REN   = 43;
pin OR    = 40;
pin PAE   = 41;
pin HF    = 38;
pin PAF   = 39;
pin FWFT  = 37; // FWFT/SI. Active HIGH
pin IR    = 36;
pin LD    = 34;
pin MRS   = 35;
pin PRS   = 32;
pin WEN   = 31;
pin SEN   = 30;

// Clock control pin mappings:
// Active HIGH unless stated otherwise
pin nPROG  = 22;
pin CLK1   = 26; // 1CLK (single-clock operation)
pin WCLK_S = 24;
pin ADC_CLK_S = 28;
pin PROG_D = DAC1;
pin STRIG  = 33;

// FIFO flags to show in status. All active low.
enum fifo_flag {
    F_IR = 0, // Input ready
    F_OR,     // Output ready
    F_PAF,    // Partially almost full
    F_PAE,    // Partially almost empty
    F_HF,     // Half full
    F_SIZE,   // The number of flags (not on FIFO)
} fifo_flags;

const pin fifo_flag_pins[] = {
    IR,
    OR,
    PAF,
    PAE,
    HF,
};

const PROGMEM char fifo_flag_names[][16] = {
    "IR",
    "OR",
    "PAF",
    "PAE",
    "HF",
};

// DAC pin mapping
pin DAC_LDAC = 46;
pin DAC_CS   = 44;

// Serial command buffer
#ifdef SCONTROL
#define SBLEN   16
char sb[SBLEN];
#endif // SCONTROL


void setup(void)
{
    // Serial communication
    Serial.begin(115200);
    Serial.print(F(
        "====================\n"
        " FIFO_P3 Time Delay \n"
        "====================\n"
        "    Reed College    \n"
        " Physics Department \n"
        "        2019        \n"   
        "====================\n"
        "    Alex Striff     \n"
        "    Edgar Perez     \n"
        "    Lucas Illing    \n"
        "====================\n"
        "Enabled features: "
        #ifdef DEBUG
        "DEBUG "
        #endif // DEBUG
        #ifdef SCREEN
        "SCREEN "
        #endif // SCREEN
        #ifdef SCONTROL
        "SCONTROL "
        #endif // SCONTROL
        #ifdef HIST
        "HIST "
        #endif // HIST
        "\n"
        "Type 'h' for help.\n\n"
        "Setting up I/O ... "
        ));

    // DAC initialization
    delay(10);
    digitalWrite(nPROG, LOW); // x. Check not flipped
    digitalWrite(DAC_LDAC, HIGH);
    delay(5);
    digitalWrite(nPROG, HIGH); // x.
    digitalWrite(DAC_LDAC, LOW);

    // Due (self) DAC initialization
    analogWriteResolution(12);
    pinMode(PROG_D, OUTPUT);
    analogWrite(PROG_D, 1u << (12 - 2)); // Half full scale

    // Clock control pins
    pinMode(nPROG,     OUTPUT);
    pinMode(CLK1,      OUTPUT);
    pinMode(WCLK_S,    OUTPUT);
    pinMode(ADC_CLK_S, OUTPUT);
    pinMode(STRIG,     OUTPUT);

    // Clock default state (single clock, not programming)
    digitalWrite(CLK1,      HIGH);
    digitalWrite(WCLK_S,    LOW);
    digitalWrite(ADC_CLK_S, LOW);
    digitalWrite(STRIG,     LOW);

    digitalWrite(nPROG, HIGH); // Disable operation while setting up.

    // FIFO pins
    pinMode(REN,  OUTPUT);
    pinMode(OR,   INPUT_PULLUP);
    pinMode(PAE,  INPUT_PULLUP);
    pinMode(HF,   INPUT_PULLUP);
    pinMode(PAF,  INPUT_PULLUP);
    pinMode(IR,   INPUT_PULLUP);
    pinMode(OE,   OUTPUT);
    pinMode(RT,   OUTPUT);
    pinMode(FWFT, OUTPUT);
    pinMode(LD,   OUTPUT);
    pinMode(MRS,  OUTPUT);
    pinMode(PRS,  OUTPUT);
    pinMode(WEN,  OUTPUT);
    pinMode(SEN,  OUTPUT);

    // FIFO default states
    digitalWrite(MRS,  HIGH);
    digitalWrite(PRS,  HIGH);
    digitalWrite(RT,   HIGH);
    //digitalWrite(FWFT, HIGH);
    digitalWrite(FWFT, LOW); // Let's try IDT mode
    digitalWrite(LD,   HIGH);
    digitalWrite(WEN,  HIGH);
    digitalWrite(REN,  HIGH);
    digitalWrite(SEN,  HIGH);
    digitalWrite(OE,   LOW);

    // DAC pins
    delay(100);
    pinMode(nPROG,    OUTPUT);
    pinMode(DAC_LDAC, OUTPUT);
    pinMode(DAC_CS,   OUTPUT);

    // More DAC initialization
    delay(10);
    pinMode(DAC_CS,   OUTPUT);
    digitalWrite(DAC_CS, HIGH);
    delay(5);
    digitalWrite(DAC_CS, LOW);
    delay(5);
    digitalWrite(DAC_CS, HIGH);
    delay(5);
    digitalWrite(DAC_CS, LOW);
    delay(10);

    // Rotary encoder pins
    pinMode(enc.btn.p, INPUT_PULLUP);
    pinMode(enc.a,     INPUT_PULLUP);
    pinMode(enc.b,     INPUT_PULLUP);
    read_encoder(&enc); // Read to initialize previous quadrature state.
    
    // Screen initialization
    #ifdef SCREEN
    if (!display.begin(SSD1306_SWITCHCAPVCC, 0x3C)) { // Address 0x3C for 128x32
        Serial.println(F("SSD1306 allocation failed. Unable to use screen."));
        screen = false;
    } else {
        screen = true;
        display.clearDisplay();
        display.cp437(true);
        display.setTextColor(WHITE);
        display.setTextSize(1);
        display.setCursor(0, 0);
        display.print(F("Time Delay Device vP3"));
        display.setCursor(0, 8);
        display.print(F("Reed College Physics"));
        display.setCursor(0, 24);
        display.print(F("2-press knob for menu"));
        display.display();

        for (uint8_t i = 0; i < SCREEN_WIDTH; i++) {
            display.drawPixel(i, 16 + (i*i / 7) % 8, WHITE);
            display.display();
        }
    }
    #endif // SCREEN

    // Do a master reset to initialize the FIFO
    Serial.print(F(" complete. Initializing FIFO:\n\t"));
    delay(5);
    master_reset(false);
    Serial.println();
    set_delay(init_words, true);
}
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

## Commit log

2020-05-22 Added assembly instructions, removed TeX logs, and reorganized docs
    [Digikey_BOM.csv, FIFO_P-B_Cu.gbr, FIFO_P-B_Mask.gbr, FIFO_P-B_SilkS.gbr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]
2020-06-01 Use Adafruit 4440 display
    [Digikey_BOM.csv]
